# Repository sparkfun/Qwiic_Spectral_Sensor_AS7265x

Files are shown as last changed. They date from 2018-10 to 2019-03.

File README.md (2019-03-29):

SparkFun Triad Spectroscopy Sensor - AS7265x (Qwiic)
===========================================================

SparkFun Triad Spectroscopy Sensor (https://www.sparkfun.com/products/15050)

[*SparkFun Triad Spectroscopy Sensor (SEN-15050)*](https://www.sparkfun.com/products/15050)

The SparkFun Triad Spectroscopy Sensor is a powerful optical inspection sensor. Three AS7265x sensors are combined alongside a visible, UV, and IR LEDs to illuminate and test various surfaces for light spectroscopy. The Triad detects 18 discrete channels of light from 372nm (UV) to 966nm (IR) enabling desktop spectroscopy.

What can you do with light spectroscopy? It’s an amazing field of study, and the SparkFun Triad brings what used to be prohibitively expensive equipment to the desktop. The AS7265x should not be confused with highly complex mass spectrometers, but the sensor array does give the user the ability to measure and characterize how different materials absorb and reflect 18 different frequencies of light.

Want to use this board using python? Checkout hwreverse [pySectralTriad](https://github.com/hwreverse/pySpectralTriad)!

**Thanks to:**

* **pySpectralTriad** for the python application

Repository Contents
-------------------

* **/Documents** - Sensor and LED datasheets
* **/Hardware** - Eagle files

Documentation
--------------

* **[Installing an Arduino Library Guide](https://learn.sparkfun.com/tutorials/installing-an-arduino-library)** - Basic information on how to install an Arduino library.
* **[Arduino Library](https://github.com/sparkfun/SparkFun_AS7265x_Arduino_Library)** - Arduino Library for the SparkFun Triad Spectroscopy Sensor.
* **[Hookup Guide](https://learn.sparkfun.com/tutorials/spectral-triad-as7265x-hookup-guide)** - Basic hookup guide for the SparkFun Triad Spectroscopy Sensor.

License Information
-------------------

This product is _**open source**_! 

Various bits of the code have different licenses applied. Anything SparkFun wrote is beerware; if you see me (or any other SparkFun employee) at the local, and you've found our code helpful, please buy us a round!

Please use, reuse, and modify these files as you see fit. Please maintain attribution to SparkFun Electronics and release anything derivative under the same license.

Distributed as-is; no warranty is given.

- Your friends at SparkFun.

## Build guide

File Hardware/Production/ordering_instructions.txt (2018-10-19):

panel size, 86x96mm
PCB thickness, 1.6mm
number of layers, 2
soldermask color, Red
silkscreen color, White
oz copper, 1oz
finish, HASL lead free
stencils, top+bottom
pcs per panel, 4

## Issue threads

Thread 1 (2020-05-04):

### ISSUE TITLE
Schematic wrong pinout

### ISSUE THREAD

**Issue by uavmax** [sparkfun/Qwiic_Spectral_Sensor_AS7265x#1]
[https://cdn.sparkfun.com/assets/3/b/0/3/e/Qwiic_Spectral_Sensor-AS7265x.pdf](url)
SCL_M and SDA_M are not 1,20(SLV1_RESN, SLV2_RESN) pins but 9,10.
no ADDR, CS_SD pins just CSN(CD_EE). INT pin 13 not 9

**Comment by nseidle** [comment]
There has been a lot of confusion created by AMS because they released early datasheets that showed incorrect pinouts. I believe those are the datasheets you are looking at. Please see the notes on the documents tab of our [product page](https://www.sparkfun.com/products/15050). Namely:

Datasheets:

* [AS7265x](https://cdn.sparkfun.com/assets/c/2/9/0/a/AS7265x_Datasheet.pdf) (Pin assignments are misleading; use Design Considerations below.)
* [Design Considerations](https://cdn.sparkfun.com/assets/8/5/f/0/3/AS7265x_Design_Considerations.pdf)

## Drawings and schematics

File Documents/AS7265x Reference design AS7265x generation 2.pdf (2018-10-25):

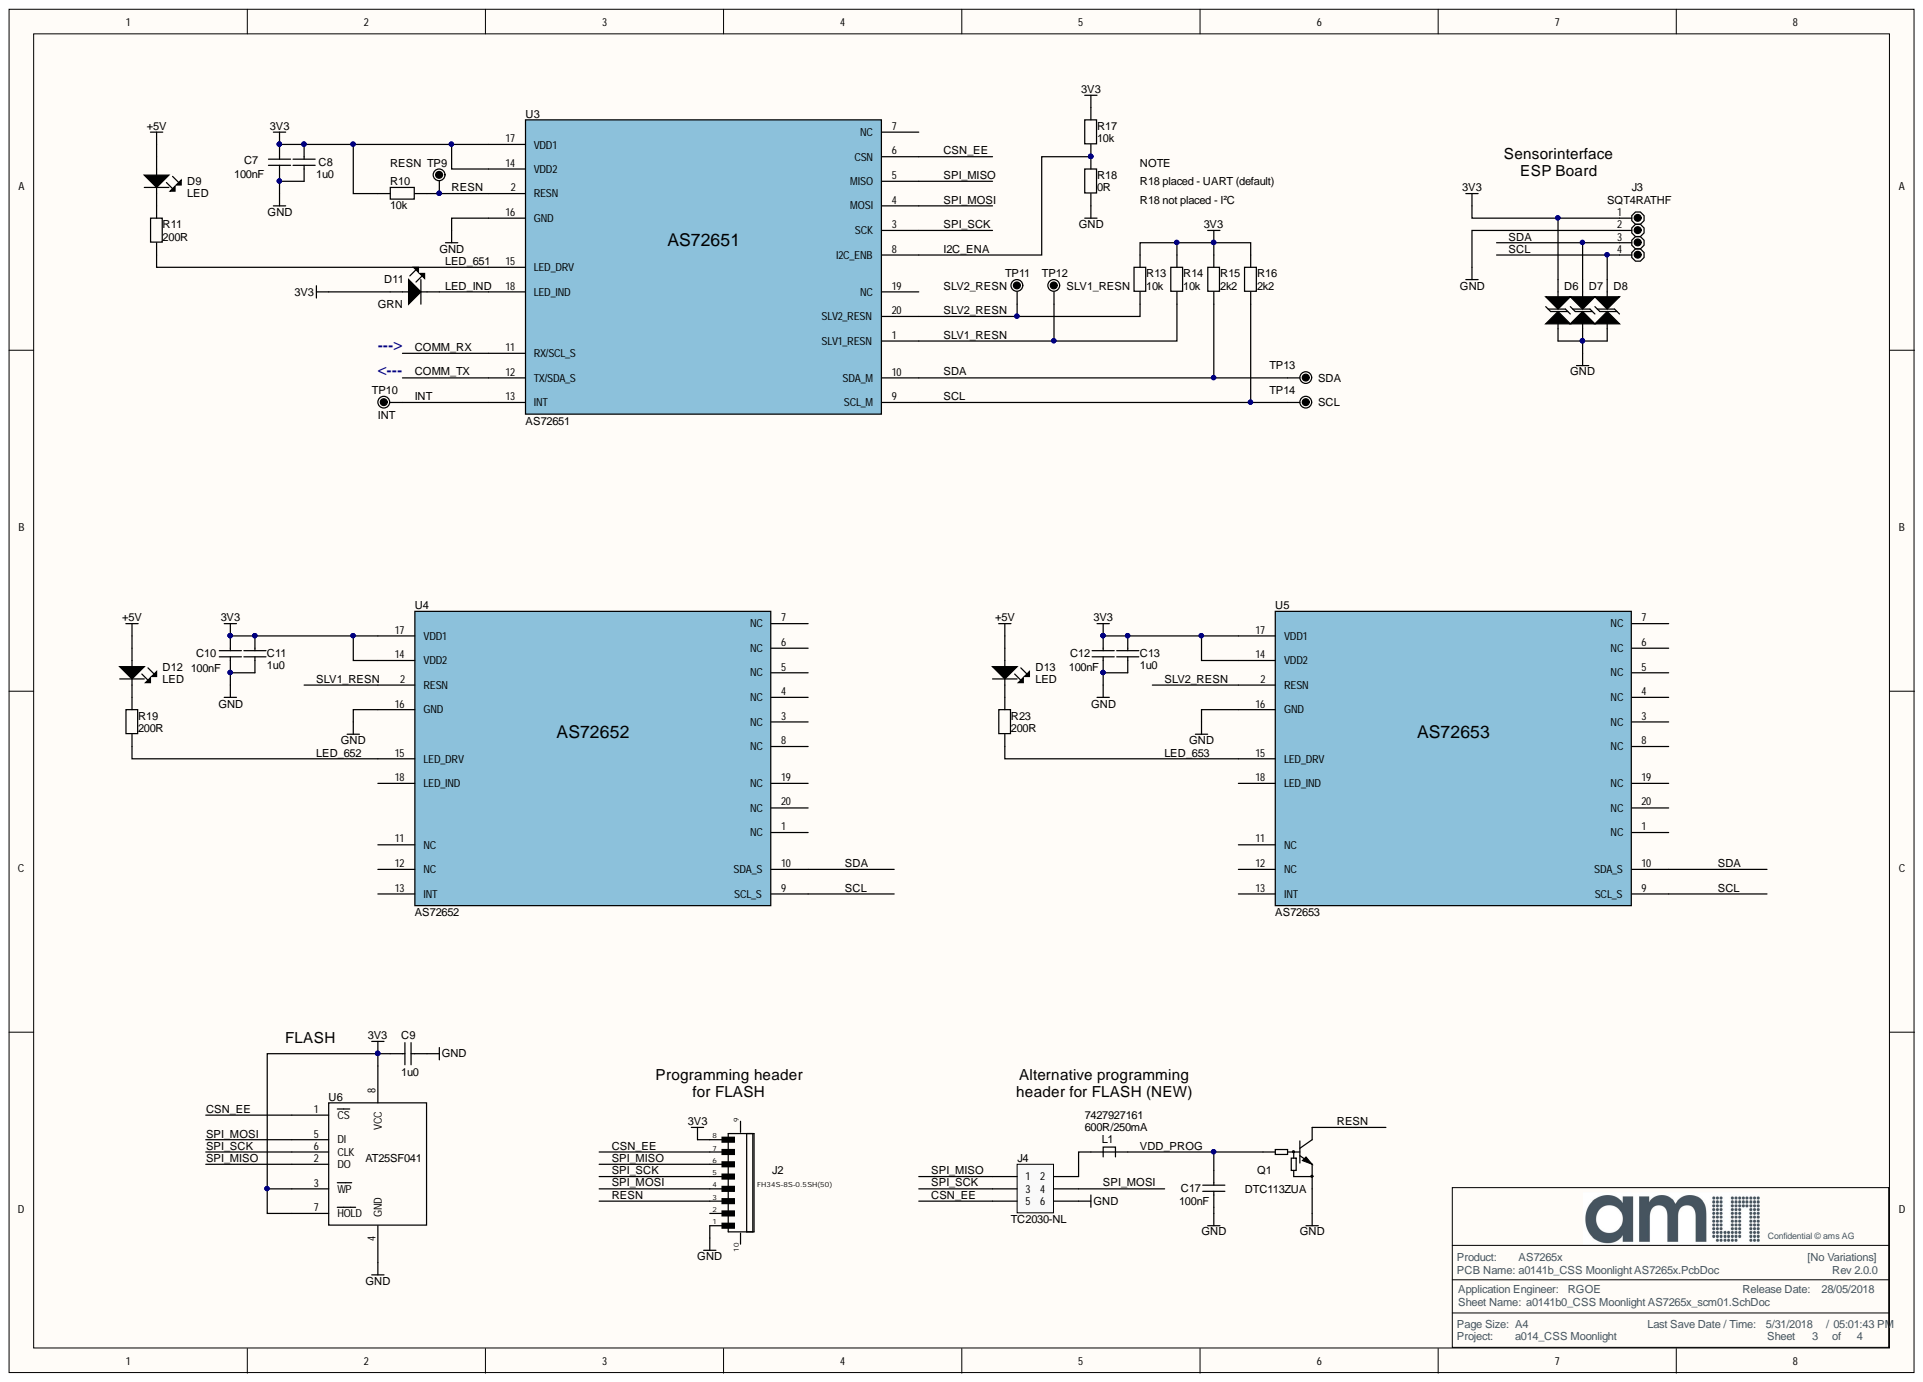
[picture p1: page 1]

VDD2 14

GND 16

Alternative programming
header for FLASH (NEW)

PCB Name:
Application Engineer: RGOE
Sheet Name: a0141b0_CSS Moonlight AS7265x_scm01.SchDoc

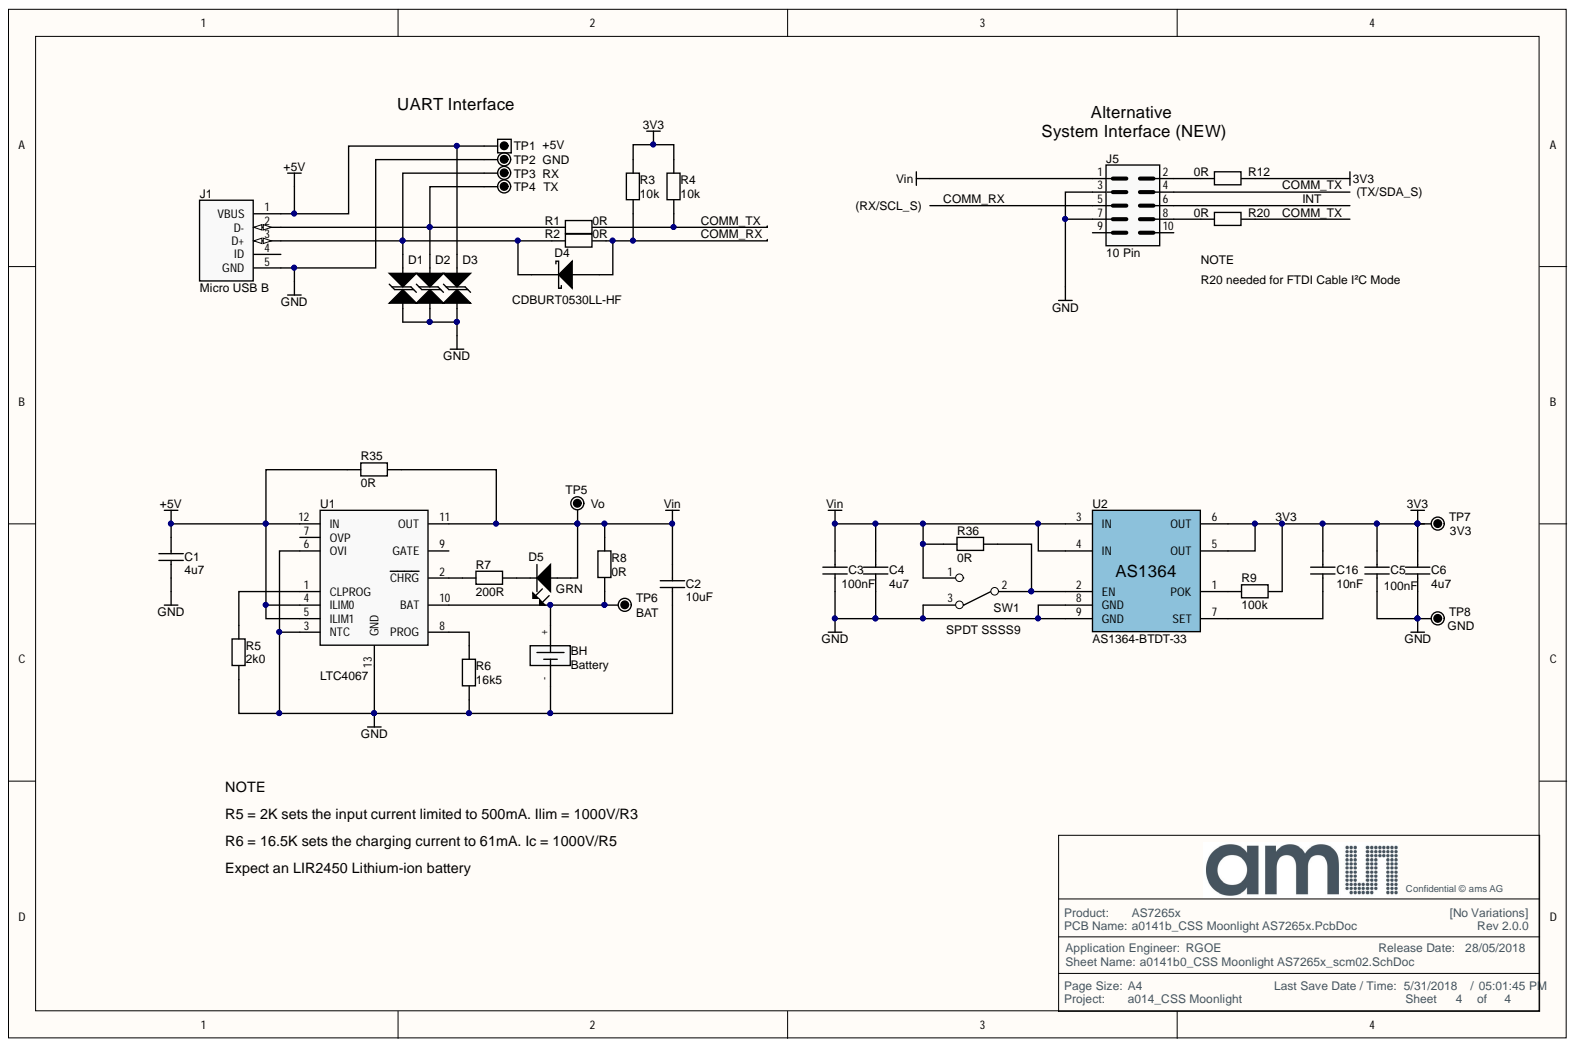
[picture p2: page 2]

NOTE
R20 needed for FTDI Cable I²C Mode

OVI 6

ILIM0 4

R5 = 2K sets the input current limited to 500mA. Ilim = 1000V/R3

R6 = 16.5K sets the charging current to 61mA. Ic = 1000V/R5

Expect an LIR2450 Lithium-ion battery

Application Engineer: RGOE
Sheet Name: a0141b0_CSS Moonlight AS7265x_scm02.SchDoc

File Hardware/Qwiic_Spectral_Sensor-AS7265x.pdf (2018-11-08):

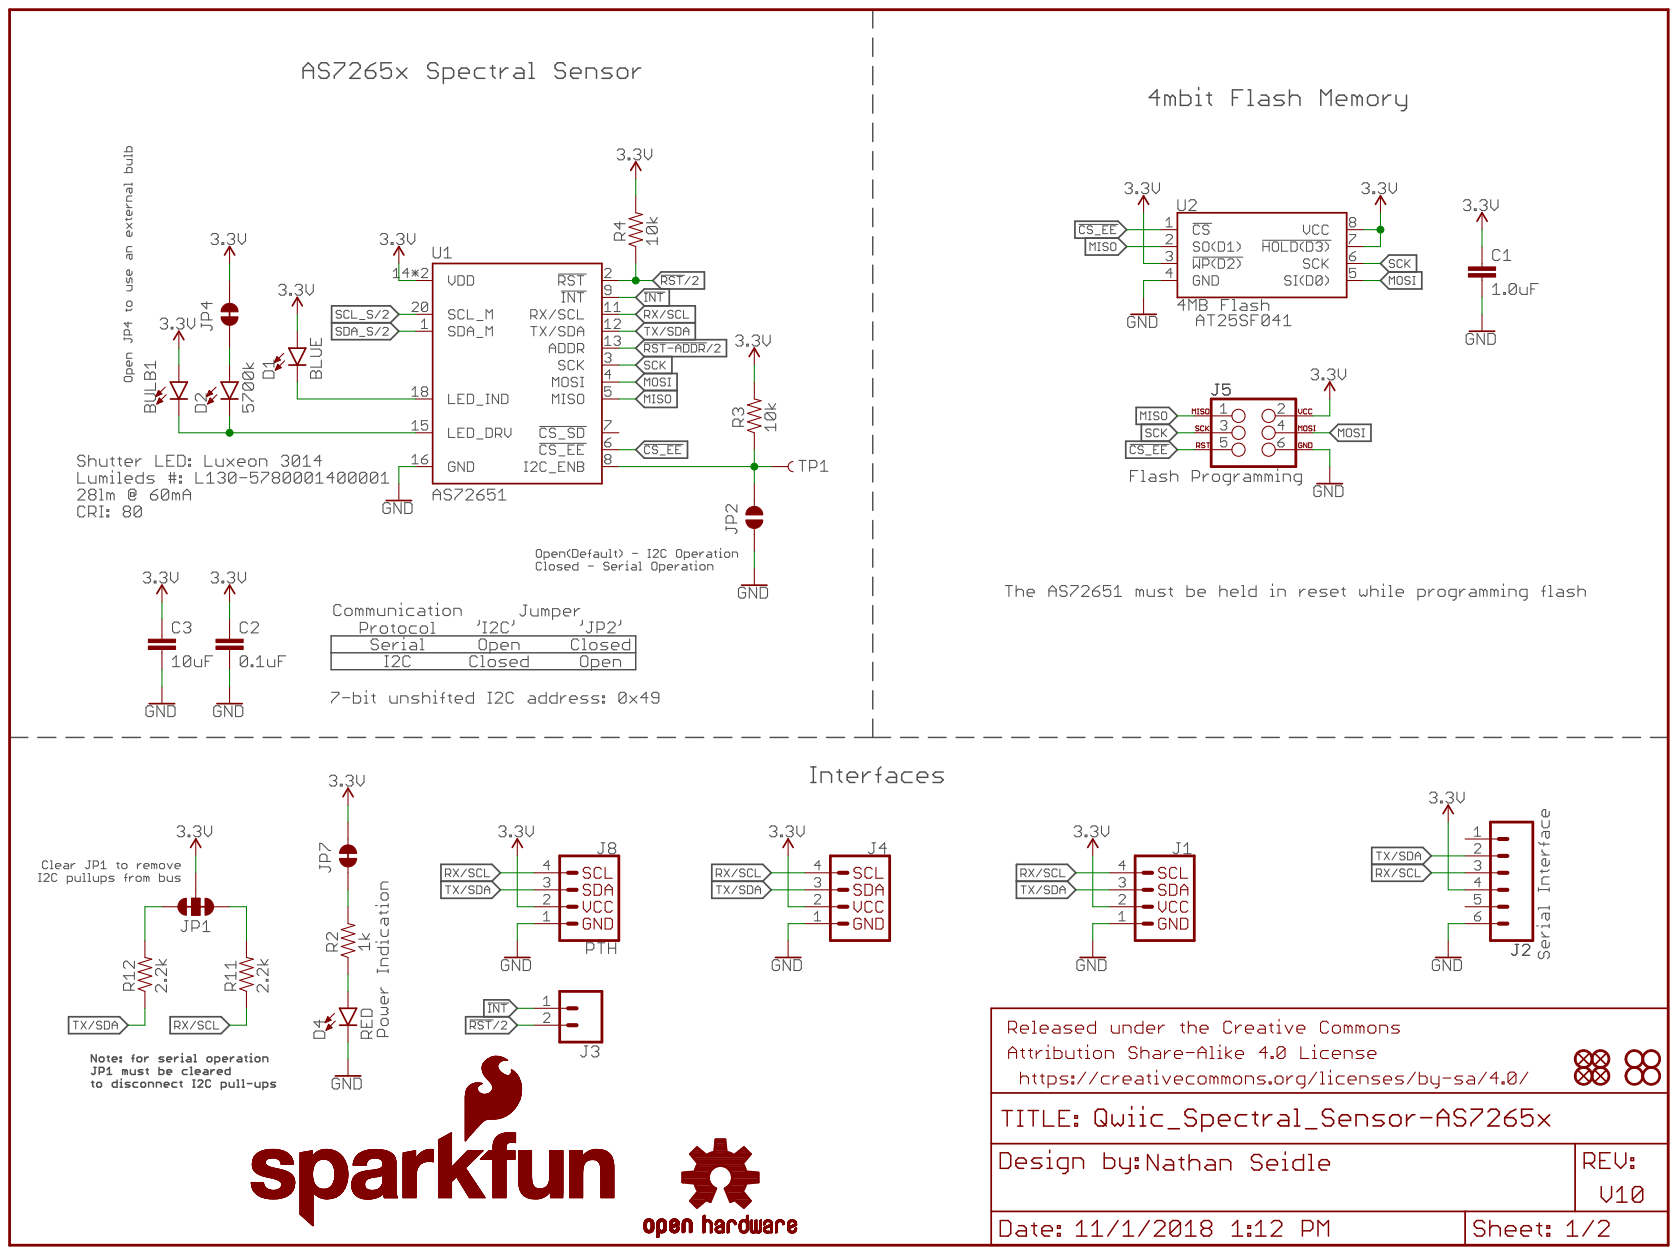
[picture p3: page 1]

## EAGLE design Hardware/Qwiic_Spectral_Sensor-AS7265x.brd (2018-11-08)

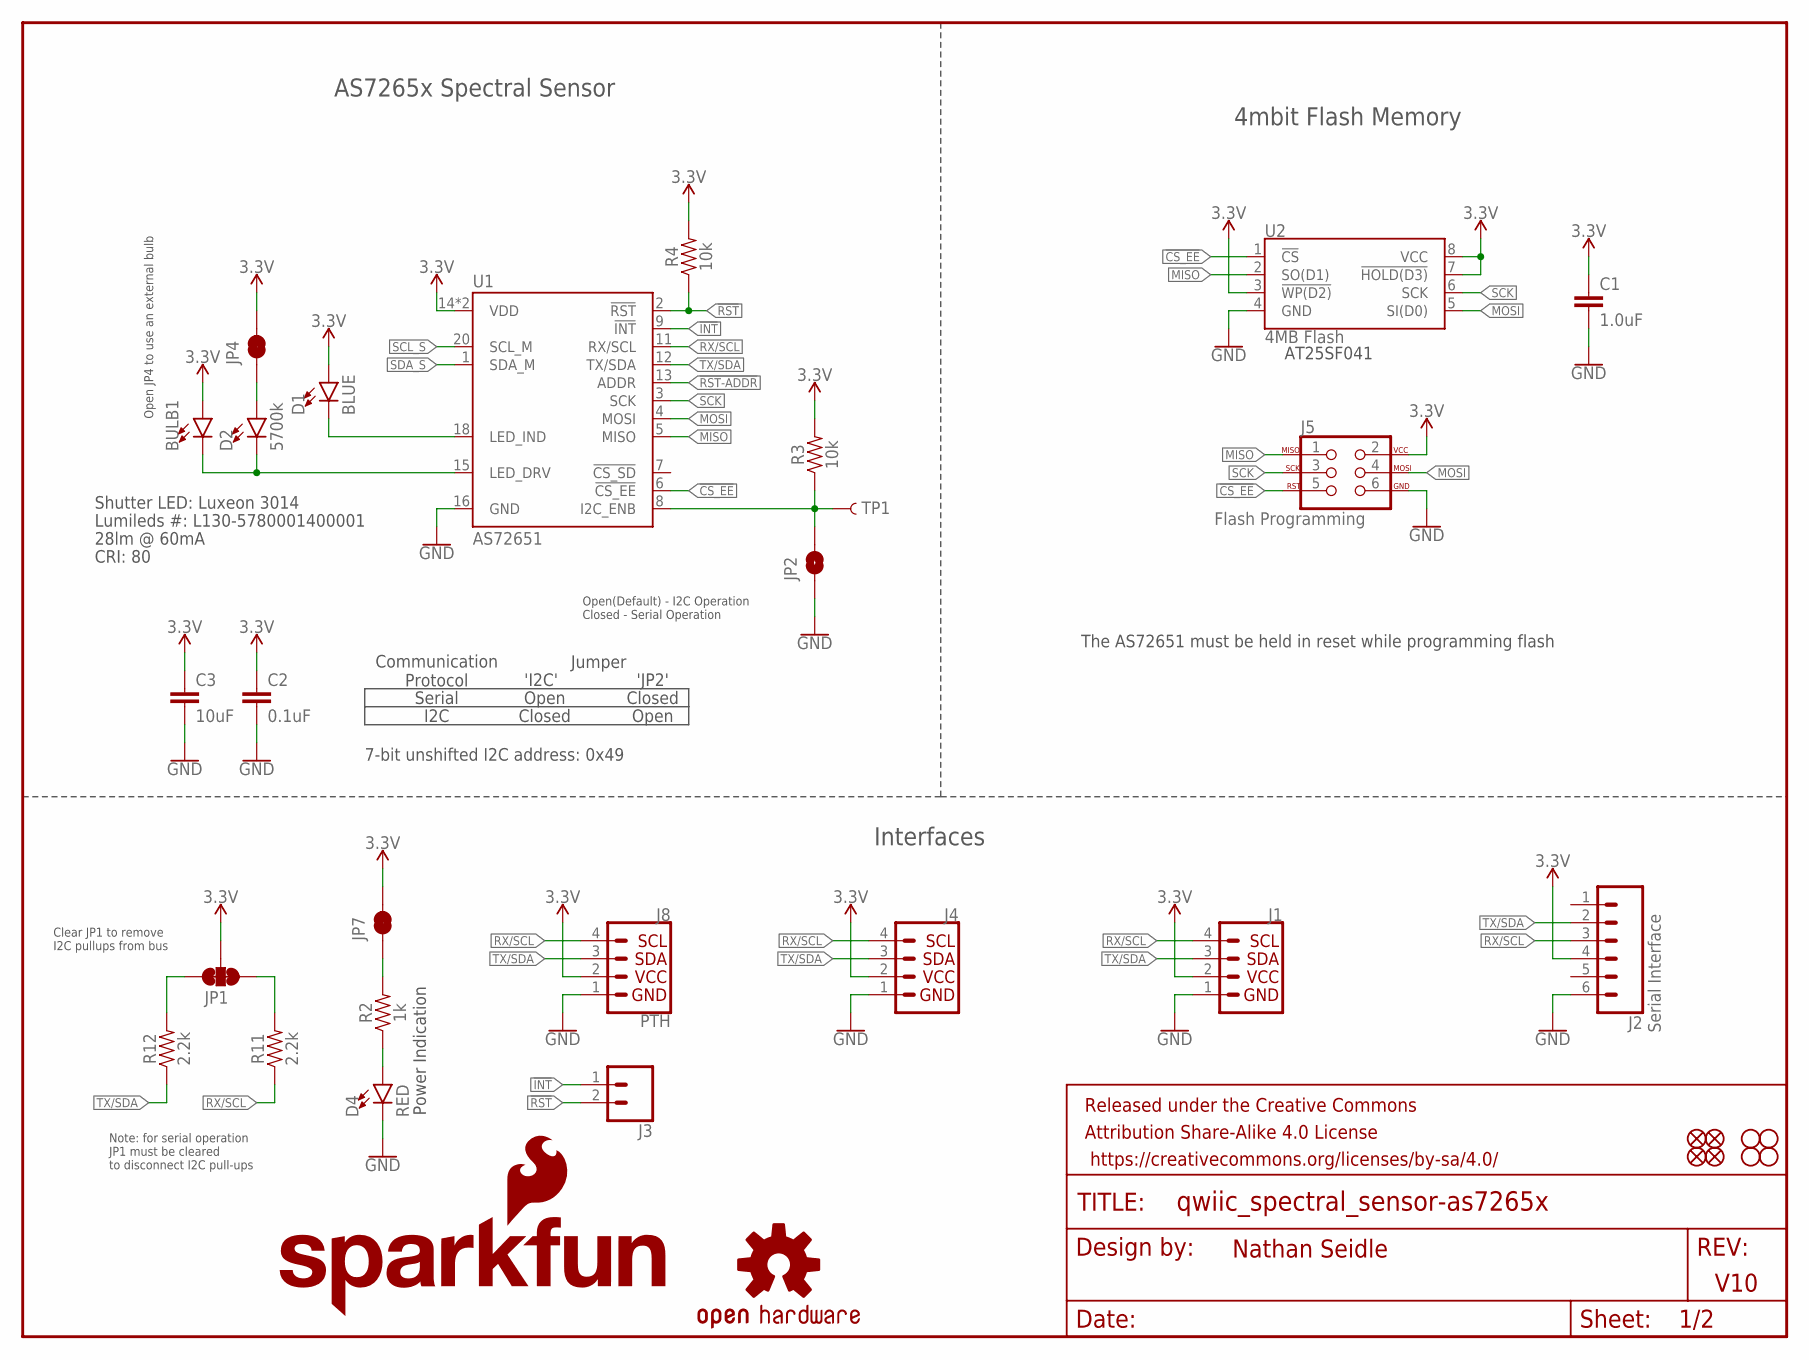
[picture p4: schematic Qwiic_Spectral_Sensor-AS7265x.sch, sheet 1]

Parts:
BULB1: LEDNS; LED_5MM_NOSILK
C1: 1.0uF; 0603
C2: 0.1uF; 0603
C3: 10uF; 0603
D1: BLUE; LED-0603
D2: 5700k; SUPER_BRIGHT_SMD_LED_3014
D4: RED; LED-0603
FD1, FD2, FD3, FD4: FIDUCIAL1X2; FIDUCIAL-1X2
FRAME1: FRAME-LETTER; CREATIVE_COMMONS
H1, H2, H3, H4: STAND-OFF
J1, J4: QWIIC_CONNECTORJS-1MM; 1X04_1MM_RA
J2: Serial Interface; 1X06_NO_SILK
J3: CONN_021X02_NO_SILK; 1X02_NO_SILK
J5: Flash Programming; 2X3_TEST_POINTS
J8: PTH; 1X04_NO_SILK
JP1: JUMPER-SMT_3_2-NC_TRACE_SILK; SMT-JUMPER_3_2-NC_TRACE_SILK
JP2: JUMPER-SMT_2_NO_SILK; SMT-JUMPER_2_NO_SILK
JP4, JP7: JUMPER-SMT_2_NC_TRACE_NO-SILK; SMT-JUMPER_2_NC_TRACE_NO-SILK
LOGO1: SFE_LOGO_NAME_FLAME.1_INCH; SFE_LOGO_NAME_FLAME_.1
LOGO4: OSHW-LOGOS; OSHW-LOGO-S
R2: 1k; 0603
R3, R4: 10k; 0603
R11, R12: 2.2k; 0603
TP1: TEST-POINT3; PAD.03X.03
U1: AS72651; LGA20
U2: 4MB Flash; SO08

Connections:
3.3V: BULB1.A, C1.1, C2.1, C3.1, D1.A, J1.2, J2.4, J4.2, J5.2, J8.2, JP1.2, JP4.2, JP7.2, R3.2, R4.2, U1.14 (VDD), U1.17 (VDD), U2.3 (!WP(D2)), U2.7 (!HOLD(D3)), U2.8 (VCC); also elsewhere on the board
!CS_EE: J5.5, U1.6 (!CS_EE), U2.1 (!CS)
!INT: J3.1, U1.9 (!INT)
!RST: J3.2, R4.1, U1.2 (!RST); also elsewhere on the board
!RST-ADDR: U1.13 (ADDR); also elsewhere on the board
GND: C1.2, C2.2, C3.2, D4.C, J1.1, J2.6, J4.1, J5.6, J8.1, JP2.1, U1.16 (GND), U2.4 (GND); also elsewhere on the board
I2C_ENB: JP2.2, R3.1, TP1.P$1, U1.8 (I2C_ENB)
LED_DRV: BULB1.K (C), D2.C, U1.15 (LED_DRV)
MISO: J5.1, U1.5 (MISO), U2.2 (SO(D1))
MOSI: J5.4, U1.4 (MOSI), U2.5 (SI(D0))
unnamed: JP7.1, R2.2
unnamed: D1.C, U1.18 (LED_IND)
unnamed: JP1.3, R12.2
unnamed: JP1.1, R11.2
unnamed: D2.A, JP4.1
unnamed: D4.A, R2.1
RX/SCL: J1.4, J2.3, J4.4, J8.4, R11.1, U1.11 (RX/SCL)
SCK: J5.3, U1.3 (SCK), U2.6 (SCK)
SCL_S: U1.20 (SCL_M); also elsewhere on the board
SDA_S: U1.1 (SDA_M); also elsewhere on the board
TX/SDA: J1.3, J2.2, J4.3, J8.3, R12.1, U1.12 (TX/SDA)

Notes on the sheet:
AS7265x Spectral Sensor
Open(Default) - I2C Operation Closed - Serial Operation
Clear JP1 to remove I2C pullups from bus
V10
Nathan Seidle
4mbit Flash Memory
Interfaces
Note: for serial operation JP1 must be cleared to disconnect I2C pull-ups
The AS72651 must be held in reset while programming flash
Open JP4 to use an external bulb
Serial
'I2C'
'JP2'
Open
Closed
Communication Protocol
I2C
Lumileds #: L130-5780001400001
Shutter LED: Luxeon 3014
28lm @ 60mA
CRI: 80
7-bit unshifted I2C address: 0x49
Power Indication
AT25SF041
Jumper

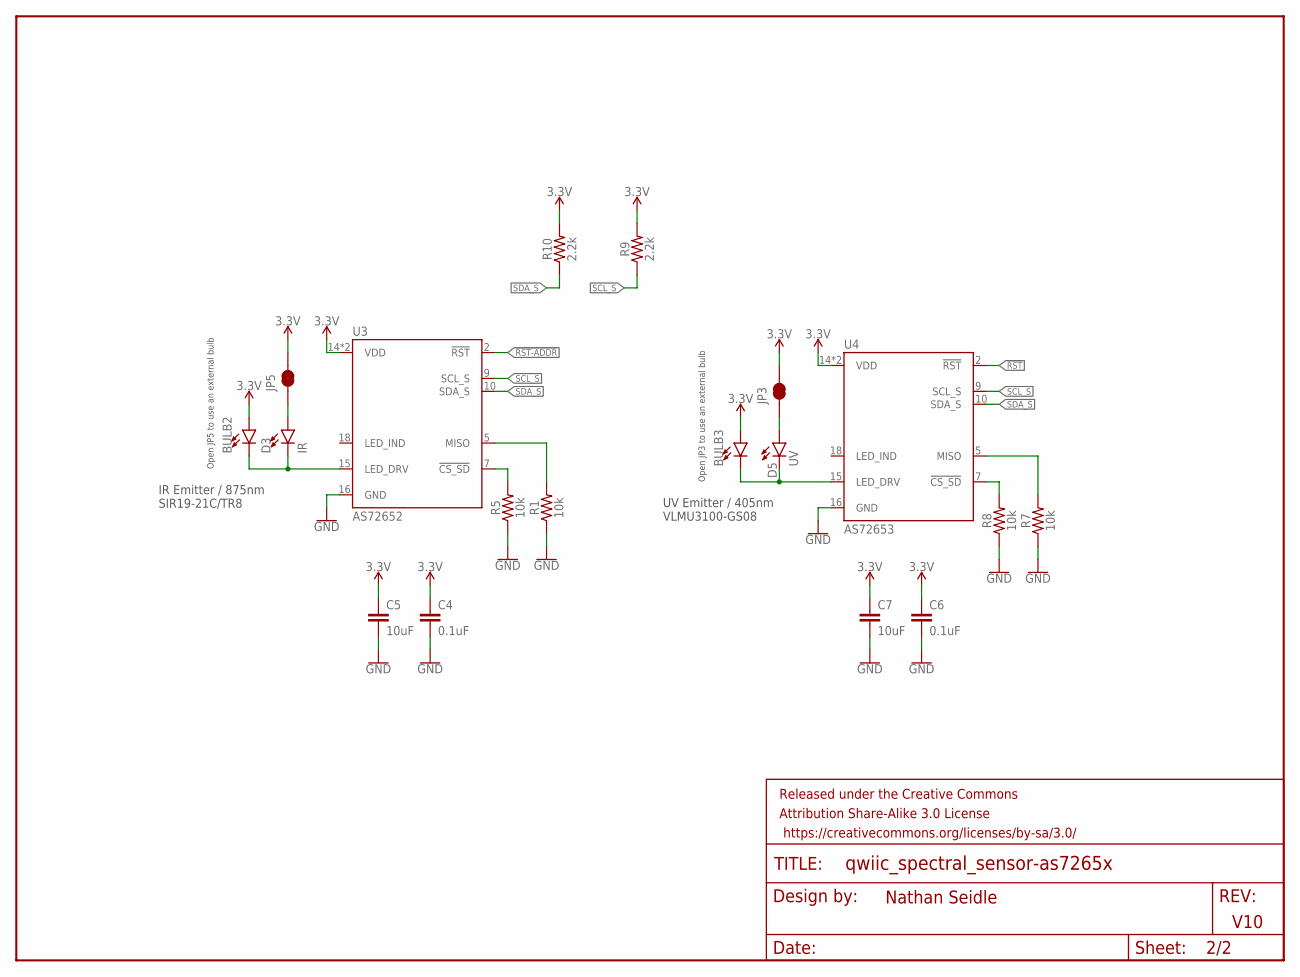
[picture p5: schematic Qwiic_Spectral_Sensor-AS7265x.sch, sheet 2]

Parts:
BULB2, BULB3: LEDNS; LED_5MM_NOSILK
C4, C6: 0.1uF; 0603
C5, C7: 10uF; 0603
D3: IR; LED-0603
D5: UV; PLCC-2
FRAME3: FRAME-LETTER; CREATIVE_COMMONS
JP3, JP5: JUMPER-SMT_2_NC_TRACE_NO-SILK; SMT-JUMPER_2_NC_TRACE_NO-SILK
R1, R5, R7, R8: 10k; 0603
R9, R10: 2.2k; 0603
U3: AS72652; LGA20
U4: AS72653; LGA20

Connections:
3.3V: BULB2.A, BULB3.A, C4.1, C5.1, C6.1, C7.1, JP3.2, JP5.2, R9.2, R10.2, U3.14 (VDD), U3.17 (VDD), U4.14 (VDD), U4.17 (VDD); also elsewhere on the board
!RST: U4.2 (!RST); also elsewhere on the board
!RST-ADDR: U3.2 (!RST); also elsewhere on the board
GND: C4.2, C5.2, C6.2, C7.2, R1.1, R5.1, R7.1, R8.1, U3.16 (GND), U4.16 (GND); also elsewhere on the board
LED_DRV1: BULB2.K (C), D3.C, U3.15 (LED_DRV)
LED_DRV2: BULB3.K (C), D5.C, U4.15 (LED_DRV)
unnamed: R5.2, U3.7 (!CS_SD)
unnamed: D3.A, JP5.1
unnamed: R1.2, U3.5 (MISO)
unnamed: D5.A, JP3.1
unnamed: R8.2, U4.7 (!CS_SD)
unnamed: R7.2, U4.5 (MISO)
SCL_S: R9.1, U3.9 (SCL_S), U4.9 (SCL_S); also elsewhere on the board
SDA_S: R10.1, U3.10 (SDA_S), U4.10 (SDA_S); also elsewhere on the board

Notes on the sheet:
Open JP5 to use an external bulb
Open JP3 to use an external bulb
IR Emitter / 875nm SIR19-21C/TR8
UV Emitter / 405nm VLMU3100-GS08
V10
Nathan Seidle

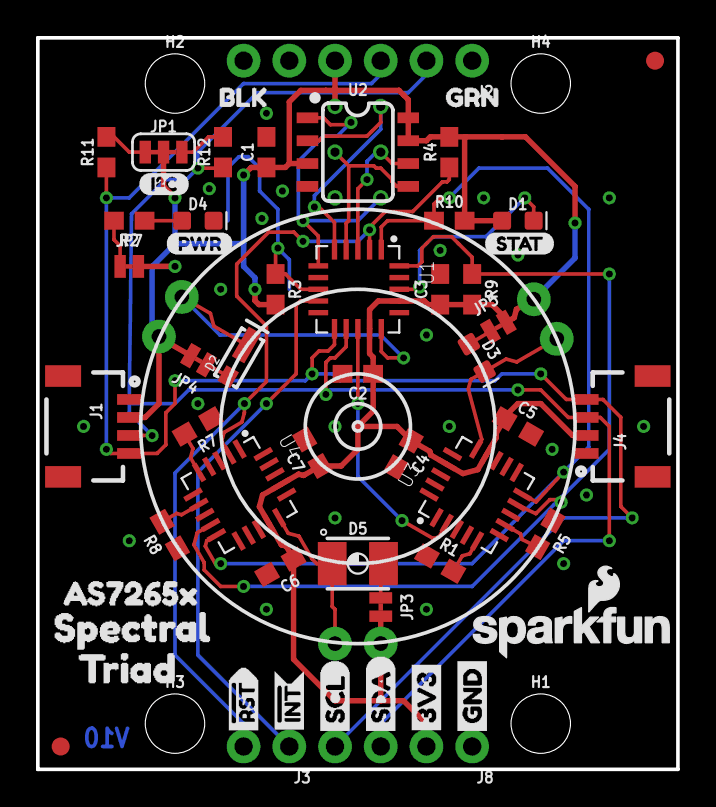
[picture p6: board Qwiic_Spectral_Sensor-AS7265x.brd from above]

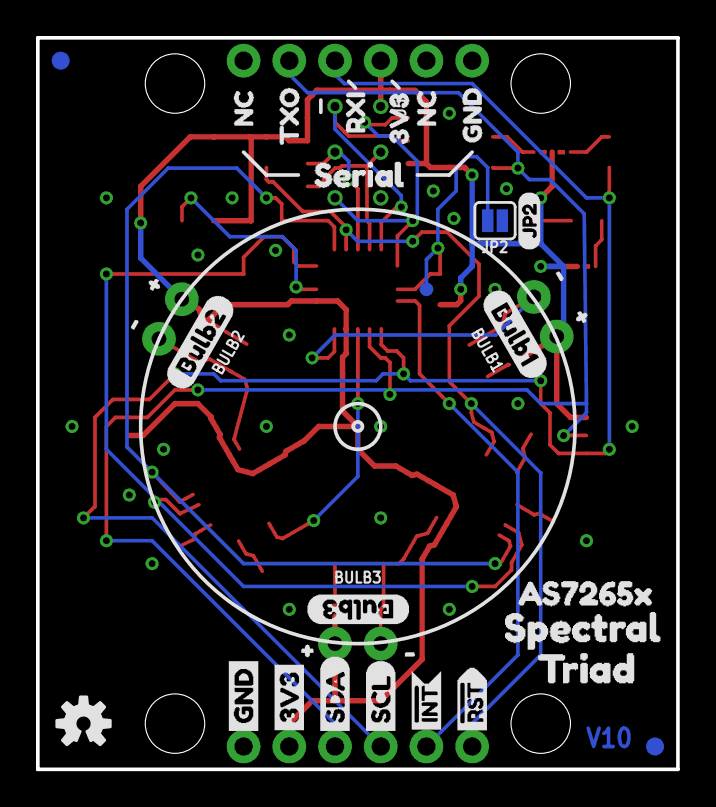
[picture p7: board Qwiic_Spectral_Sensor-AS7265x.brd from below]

Board: 2 copper layers, 35.6 x 40.6 mm, 95 parts (35 on the bottom side), 29 nets.

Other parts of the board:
U$1, U$36, U$37: #0
U$2: I_SUPER2_C-()-03
U$3: PWR-()-03
U$4, U$14: AS7265X0
U$5: BULB15
U$6: BULB26
U$7: BULB37
U$8: JP20
U$9, U$13: SPECTRAL1
U$10: STAT4
U$11, U$12: TRIAD2
U$15: 3V33
U$16: BLK7
U$17: GND5
U$18: GRN6
U$19, U$20: NC4
U$21: RXI2
U$22: SERIAL0
U$23: TXO1
U$24, U$31: 3V3-04
U$25, U$30: GND-04
U$26, U$32: SDA-[)
U$27, U$33: SCL-[)
U$28, U$34: INT#-[<-04
U$29, U$35: RST#-[>-04
U$38, U$39, U$40: #1

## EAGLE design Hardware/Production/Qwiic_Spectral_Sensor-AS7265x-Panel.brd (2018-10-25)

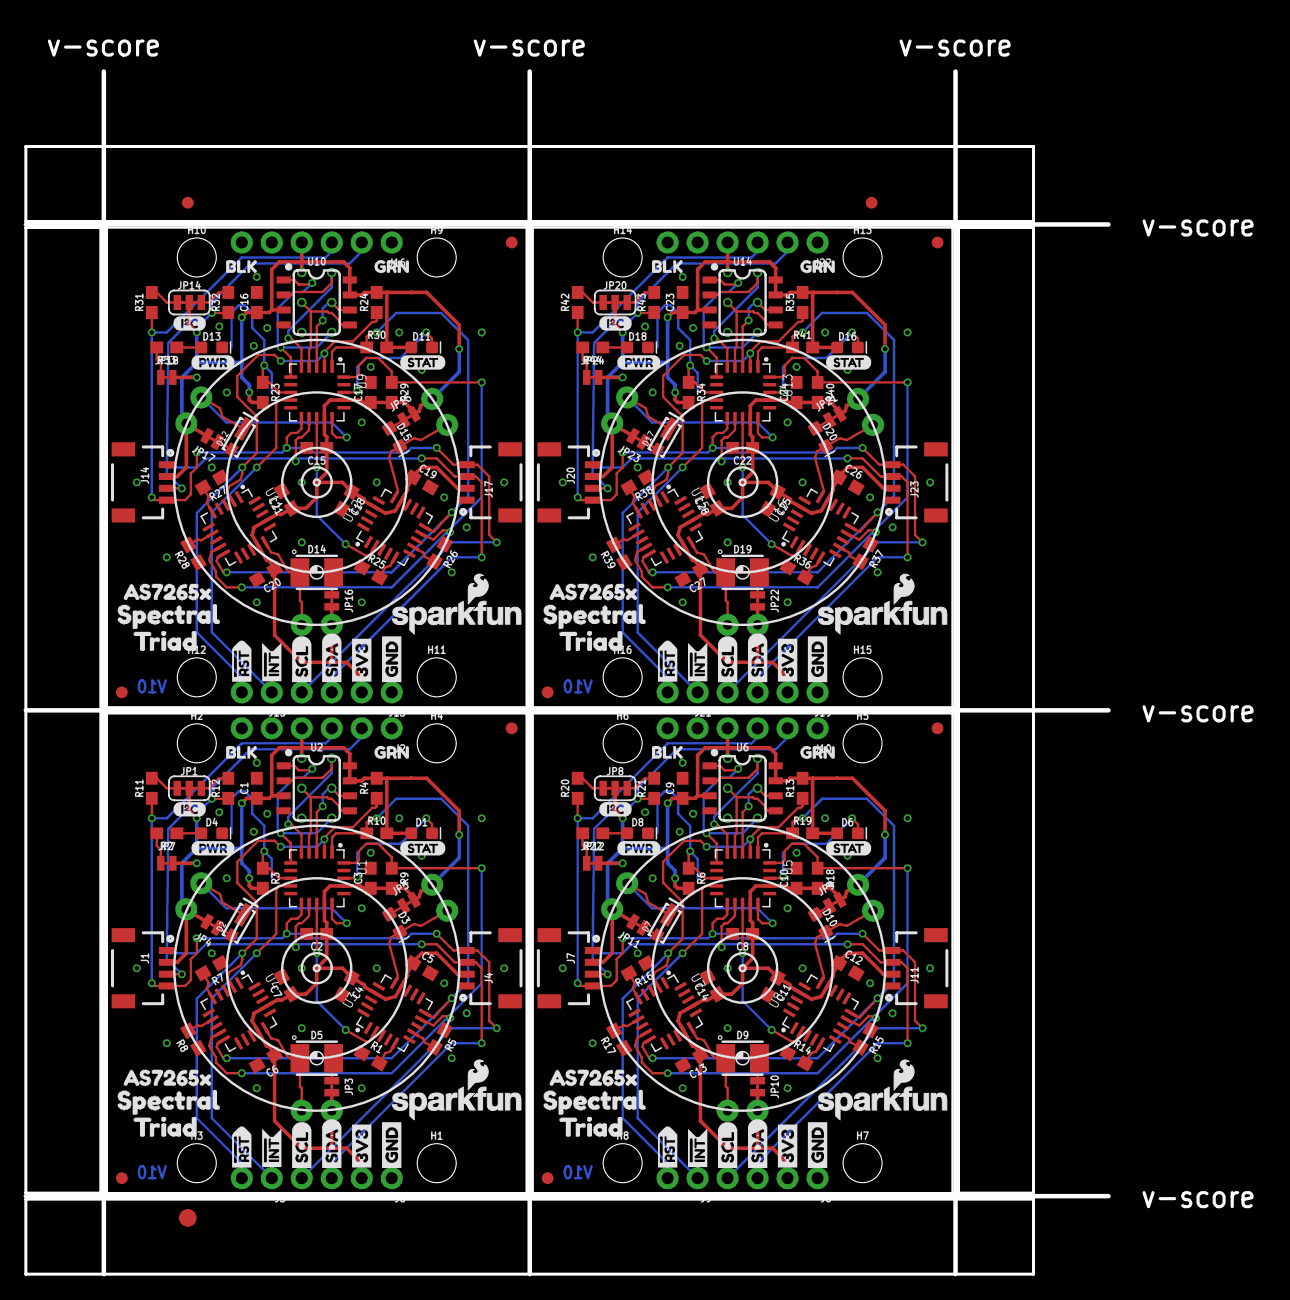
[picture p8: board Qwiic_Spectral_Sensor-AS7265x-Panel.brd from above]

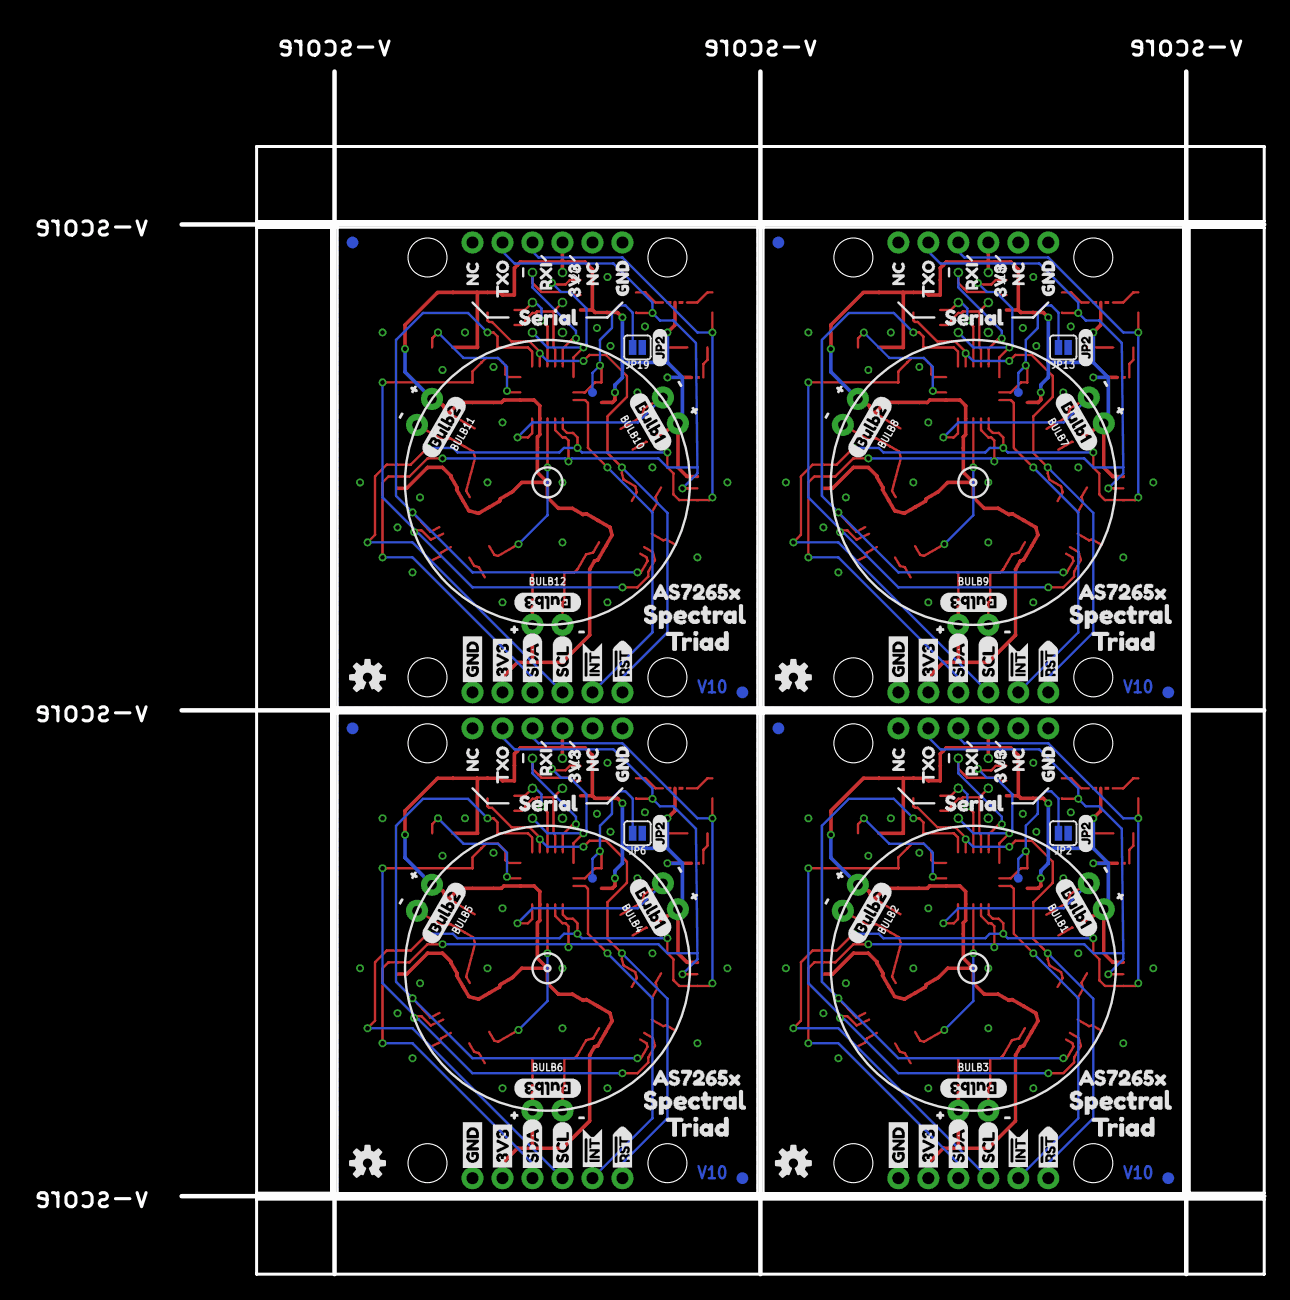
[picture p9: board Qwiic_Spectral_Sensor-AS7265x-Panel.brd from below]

Board: 2 copper layers, 91.7 x 101.9 mm, 375 parts (140 on the bottom side), 116 nets.

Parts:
BULB1, BULB2, BULB3, BULB4, BULB5, BULB6, BULB7, BULB8, BULB9, BULB10, BULB11, BULB12: LED_5MM_NOSILK
C1, C9, C16, C23: 1.0uF; 0603
C2, C4, C6, C8, C11, C13, C15, C18, C20, C22, C25, C27: 0.1uF; 0603
C3, C5, C7, C10, C12, C14, C17, C19, C21, C24, C26, C28: 10uF; 0603
D1, D6, D11, D16: BLUE; LED-0603
D2, D7, D12, D17: 5700k; SUPER_BRIGHT_SMD_LED_3014
D3, D10, D15, D20: IR; LED-0603
D4, D8, D13, D18: RED; LED-0603
D5, D9, D14, D19: UV; PLCC-2
E$1, E$2: FIDUCIAL-1X2
E$3: FIDUCIAL-1.5X3
FD1, FD2, FD3, FD4, FD5, FD6, FD7, FD8, FD9, FD10, FD11, FD12, FD13, FD14, FD15, FD16: FIDUCIAL1X2; FIDUCIAL-1X2
H1, H2, H3, H4, H5, H6, H7, H8, H9, H10, H11, H12, H13, H14, H15, H16: STAND-OFF
J1, J4, J7, J11, J14, J17, J20, J23: 1X04_1MM_RA
J2, J10, J16, J22: Serial Interface; 1X06_NO_SILK
J3, J9, J15, J21: 1X02_NO_SILK
J5, J12, J18, J24: Flash Programming; 2X3_TEST_POINTS
J6, J8, J13, J19: PTH; 1X04_NO_SILK
JP1, JP8, JP14, JP20: SMT-JUMPER_3_2-NC_TRACE_SILK
JP2, JP6, JP13, JP19: SMT-JUMPER_2_NO_SILK
JP3, JP4, JP5, JP7, JP9, JP10, JP11, JP12, JP15, JP16, JP17, JP18, JP21, JP22, JP23, JP24: SMT-JUMPER_2_NC_TRACE_NO-SILK
LOGO1, LOGO3, LOGO6, LOGO8: SFE_LOGO_NAME_FLAME.1_INCH; SFE_LOGO_NAME_FLAME_.1
LOGO2, LOGO4, LOGO5, LOGO7: OSHW-LOGOS; OSHW-LOGO-S
R1, R3, R4, R5, R6, R7, R8, R13, R14, R15, R16, R17, R23, R24, R25, R26, R27, R28, R34, R35, R36, R37, R38, R39: 10k; 0603
R2, R22, R33, R44: 1k; 0603
R9, R10, R11, R12, R18, R19, R20, R21, R29, R30, R31, R32, R40, R41, R42, R43: 2.2k; 0603
TP1, TP2, TP3, TP4: PAD.03X.03
U1, U5, U9, U13: AS72651; LGA20
U2, U6, U10, U14: 4MB Flash; SO08
U3, U8, U12, U16: AS72652; LGA20
U4, U7, U11, U15: AS72653; LGA20
U$1, U$36, U$37, U$75, U$76, U$77, U$115, U$116, U$117, U$155, U$156, U$157: #0
U$2, U$41, U$81, U$121: I_SUPER2_C-()-03
U$3, U$42, U$82, U$122: PWR-()-03
U$4, U$14, U$43, U$52, U$83, U$92, U$123, U$132: AS7265X0
U$5, U$44, U$84, U$124: BULB15
U$6, U$45, U$85, U$125: BULB26
U$7, U$46, U$86, U$126: BULB37
U$8, U$62, U$102, U$142: JP20
U$9, U$13, U$47, U$51, U$87, U$91, U$127, U$131: SPECTRAL1
U$10, U$48, U$88, U$128: STAT4
U$11, U$12, U$49, U$50, U$89, U$90, U$129, U$130: TRIAD2
U$15, U$53, U$93, U$133: 3V33
U$16, U$54, U$94, U$134: BLK7
U$17, U$55, U$95, U$135: GND5
U$18, U$56, U$96, U$136: GRN6
U$19, U$20, U$57, U$58, U$97, U$98, U$137, U$138: NC4
U$21, U$59, U$99, U$139: RXI2
U$22, U$60, U$100, U$140: SERIAL0
U$23, U$61, U$101, U$141: TXO1
U$24, U$31, U$63, U$70, U$103, U$110, U$143, U$150: 3V3-04
U$25, U$30, U$64, U$69, U$104, U$109, U$144, U$149: GND-04
U$26, U$32, U$65, U$71, U$105, U$111, U$145, U$151: SDA-[)
U$27, U$33, U$66, U$72, U$106, U$112, U$146, U$152: SCL-[)
U$28, U$34, U$67, U$73, U$107, U$113, U$147, U$153: INT#-[<-04
U$29, U$35, U$68, U$74, U$108, U$114, U$148, U$154: RST#-[>-04
U$38, U$39, U$40, U$78, U$79, U$80, U$118, U$119, U$120, U$158, U$159, U$160: #1

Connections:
3.3V: BULB1.A, BULB2.A, BULB3.A, C1.1, C2.1, C3.1, C4.1, C5.1, C6.1, C7.1, D1.A, J1.2, J2.4, J4.2, J5.2, J8.2, JP1.2, JP3.2, JP4.2, JP5.2, JP7.2, R3.2, R4.2, R9.2, R10.2, U1.14, U1.17, U2.3, U2.7, U2.8, U3.14, U3.17, U4.14, U4.17
3.3V1: BULB4.A, BULB5.A, BULB6.A, C8.1, C9.1, C10.1, C11.1, C12.1, C13.1, C14.1, D6.A, J6.2, J7.2, J10.4, J11.2, J12.2, JP8.2, JP9.2, JP10.2, JP11.2, JP12.2, R6.2, R13.2, R18.2, R19.2, U5.14, U5.17, U6.3, U6.7, U6.8, U7.14, U7.17, U8.14, U8.17
3.3V2: BULB7.A, BULB8.A, BULB9.A, C15.1, C16.1, C17.1, C18.1, C19.1, C20.1, C21.1, D11.A, J13.2, J14.2, J16.4, J17.2, J18.2, JP14.2, JP15.2, JP16.2, JP17.2, JP18.2, R23.2, R24.2, R29.2, R30.2, U9.14, U9.17, U10.3, U10.7, U10.8, U11.14, U11.17, U12.14, U12.17
3.3V3: BULB10.A, BULB11.A, BULB12.A, C22.1, C23.1, C24.1, C25.1, C26.1, C27.1, C28.1, D16.A, J19.2, J20.2, J22.4, J23.2, J24.2, JP20.2, JP21.2, JP22.2, JP23.2, JP24.2, R34.2, R35.2, R40.2, R41.2, U13.14, U13.17, U14.3, U14.7, U14.8, U15.14, U15.17, U16.14, U16.17
!CS_EE: J5.5, U1.6, U2.1
!CS_EE1: J12.5, U5.6, U6.1
!CS_EE2: J18.5, U9.6, U10.1
!CS_EE3: J24.5, U13.6, U14.1
!INT: J3.1, U1.9
!INT1: J9.1, U5.9
!INT2: J15.1, U9.9
!INT3: J21.1, U13.9
!RST: J3.2, R4.1, U1.2, U4.2
!RST1: J9.2, R13.1, U5.2, U7.2
!RST2: J15.2, R24.1, U9.2, U11.2
!RST3: J21.2, R35.1, U13.2, U15.2
!RST-ADDR: U1.13, U3.2
!RST-ADDR1: U5.13, U8.2
!RST-ADDR2: U9.13, U12.2
!RST-ADDR3: U13.13, U16.2
GND: C1.2, C2.2, C3.2, C4.2, C5.2, C6.2, C7.2, D4.C, J1.1, J2.6, J4.1, J5.6, J8.1, JP2.1, R1.1, R5.1, R7.1, R8.1, U1.16, U2.4, U3.16, U4.16
GND1: C8.2, C9.2, C10.2, C11.2, C12.2, C13.2, C14.2, D8.C, J6.1, J7.1, J10.6, J11.1, J12.6, JP6.1, R14.1, R15.1, R16.1, R17.1, U5.16, U6.4, U7.16, U8.16
GND2: C15.2, C16.2, C17.2, C18.2, C19.2, C20.2, C21.2, D13.C, J13.1, J14.1, J16.6, J17.1, J18.6, JP13.1, R25.1, R26.1, R27.1, R28.1, U9.16, U10.4, U11.16, U12.16
GND3: C22.2, C23.2, C24.2, C25.2, C26.2, C27.2, C28.2, D18.C, J19.1, J20.1, J22.6, J23.1, J24.6, JP19.1, R36.1, R37.1, R38.1, R39.1, U13.16, U14.4, U15.16, U16.16
I2C_ENB: JP2.2, R3.1, TP1.P$1, U1.8
I2C_ENB1: JP6.2, R6.1, TP2.P$1, U5.8
I2C_ENB2: JP13.2, R23.1, TP3.P$1, U9.8
I2C_ENB3: JP19.2, R34.1, TP4.P$1, U13.8
LED_DRV: BULB1.K, D2.C, U1.15
LED_DRV1: BULB2.K, D3.C, U3.15
LED_DRV2: BULB3.K, D5.C, U4.15
LED_DRV3: BULB4.K, D7.C, U5.15
LED_DRV4: BULB5.K, D10.C, U8.15
LED_DRV5: BULB6.K, D9.C, U7.15
LED_DRV6: BULB7.K, D12.C, U9.15
LED_DRV7: BULB8.K, D15.C, U12.15
LED_DRV8: BULB9.K, D14.C, U11.15
LED_DRV9: BULB10.K, D17.C, U13.15
LED_DRV10: BULB11.K, D20.C, U16.15
LED_DRV11: BULB12.K, D19.C, U15.15
MISO: J5.1, U1.5, U2.2
MISO1: J12.1, U5.5, U6.2
MISO2: J18.1, U9.5, U10.2
MISO3: J24.1, U13.5, U14.2
MOSI: J5.4, U1.4, U2.5
MOSI1: J12.4, U5.4, U6.5
MOSI2: J18.4, U9.4, U10.5
MOSI3: J24.4, U13.4, U14.5
unnamed: JP7.1, R2.2
unnamed: D1.C, U1.18
unnamed: R5.2, U3.7
unnamed: JP1.3, R12.2
unnamed: JP1.1, R11.2
unnamed: D2.A, JP4.1
unnamed: D4.A, R2.1
unnamed: D3.A, JP5.1
unnamed: R1.2, U3.5
unnamed: JP8.3, R21.2
unnamed: D5.A, JP3.1
unnamed: R8.2, U4.7
unnamed: R7.2, U4.5
unnamed: JP8.1, R20.2
unnamed: D6.C, U5.18
unnamed: D7.A, JP11.1
unnamed: D10.A, JP9.1
unnamed: R15.2, U8.7
unnamed: R14.2, U8.5
unnamed: D9.A, JP10.1
unnamed: R17.2, U7.7
unnamed: R16.2, U7.5
unnamed: JP12.1, R22.2
unnamed: D8.A, R22.1
unnamed: JP14.3, R32.2
unnamed: JP14.1, R31.2
unnamed: D11.C, U9.18
unnamed: D12.A, JP17.1
unnamed: D15.A, JP15.1
unnamed: R26.2, U12.7
unnamed: R25.2, U12.5
unnamed: D14.A, JP16.1
unnamed: R28.2, U11.7
unnamed: R27.2, U11.5
unnamed: JP18.1, R33.2
unnamed: D13.A, R33.1
unnamed: JP20.3, R43.2
unnamed: JP20.1, R42.2
unnamed: D16.C, U13.18
unnamed: D17.A, JP23.1
unnamed: D20.A, JP21.1
unnamed: R37.2, U16.7
unnamed: R36.2, U16.5
unnamed: D19.A, JP22.1
unnamed: R39.2, U15.7
unnamed: R38.2, U15.5
unnamed: JP24.1, R44.2
unnamed: D18.A, R44.1
RX/SCL: J1.4, J2.3, J4.4, J8.4, R11.1, U1.11
RX/SCL1: J6.4, J7.4, J10.3, J11.4, R20.1, U5.11
RX/SCL2: J13.4, J14.4, J16.3, J17.4, R31.1, U9.11
RX/SCL3: J19.4, J20.4, J22.3, J23.4, R42.1, U13.11
SCK: J5.3, U1.3, U2.6
SCK1: J12.3, U5.3, U6.6
SCK2: J18.3, U9.3, U10.6
SCK3: J24.3, U13.3, U14.6
SCL_S: R9.1, U1.20, U3.9, U4.9
SCL_S1: R18.1, U5.20, U7.9, U8.9
SCL_S2: R29.1, U9.20, U11.9, U12.9
SCL_S3: R40.1, U13.20, U15.9, U16.9
SDA_S: R10.1, U1.1, U3.10, U4.10
SDA_S1: R19.1, U5.1, U7.10, U8.10
SDA_S2: R30.1, U9.1, U11.10, U12.10
SDA_S3: R41.1, U13.1, U15.10, U16.10
TX/SDA: J1.3, J2.2, J4.3, J8.3, R12.1, U1.12
TX/SDA1: J6.3, J7.3, J10.2, J11.3, R21.1, U5.12
TX/SDA2: J13.3, J14.3, J16.2, J17.3, R32.1, U9.12
TX/SDA3: J19.3, J20.3, J22.2, J23.3, R43.1, U13.12

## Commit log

2018-10-15 Updating with Buzzard labels. Change logo to SparkFun. Change v to v10.
    [Qwiic_Spectral_Sensor-AS7265x.brd, Qwiic_Spectral_Sensor-AS7265x.sch]
2018-10-15 Removing old files
    [Q_Spec_Triad.GBL, Q_Spec_Triad.GBO, Q_Spec_Triad.GBS, Q_Spec_Triad.GKO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]
2018-10-16 Adding prod_ids to new parts
    [Qwiic_Spectral_Sensor-AS7265x.brd, Qwiic_Spectral_Sensor-AS7265x.sch]
2018-10-16 Moving board to origin
    [Qwiic_Spectral_Sensor-AS7265x.brd]
2018-10-16 Silk changes before panelization
    [Qwiic_Spectral_Sensor-AS7265x-BottomJig.brd, Qwiic_Spectral_Sensor-AS7265x-BottomJig.sch, Qwiic_Spectral_Sensor-AS7265x-MiddleJig.brd, Qwiic_Spectral_Sensor-AS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]
2018-10-16 Adding LED disconnect jumpers
    [Qwiic_Spectral_Sensor-AS7265x.brd, Qwiic_Spectral_Sensor-AS7265x.sch]
2018-10-16 Commit before panels
    [Qwiic_Spectral_Sensor-AS7265x.brd, Qwiic_Spectral_Sensor-AS7265x.sch]
2018-10-19 Adding panel
    [Qwiic_Spectral_Sensor-AS7265x-Panel.GBL, Qwiic_Spectral_Sensor-AS7265x-Panel.GBO, Qwiic_Spectral_Sensor-AS7265x-Panel.GBP, Qwiic_Spectral_Sensor-AS7265x-Panel.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]
2018-10-19 Adding Jig - It's called real jig to differentiate it from the Jig directory that is auto-generated a lot during jig testing.
    [Qwiic_Spectral_Sensor-AS7265x-BottomJig.brd, Qwiic_Spectral_Sensor-AS7265x-BottomJig.sch, Qwiic_Spectral_Sensor-AS7265x-MiddleJig.brd, Qwiic_Spectral_Sensor-AS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]
2018-10-19 Removing unneeded pass-through holes
    [Qwiic_Spectral_Sensor-AS7265x-BottomJig.brd, Qwiic_Spectral_Sensor-AS7265x-MiddleJig.brd]
2018-10-25 Intermediate committ. Probably ignore the jig files.
    [AS7265_CommandSet.xlsx, Qwiic_Spectral_Sensor-AS7265x-BottomJig.brd, Qwiic_Spectral_Sensor-AS7265x-BottomJig.sch, Qwiic_Spectral_Sensor-AS7265x-MiddleJig.GBL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]
2018-10-31 Adding test jig firmware
    [Qwiic_Spectral_Sensor-AS7265x-Offset-BottomJig.brd, Qwiic_Spectral_Sensor-AS7265x.brd]
2018-11-01 Update to schematic table. Update to readme.
    [Qwiic_Spectral_Sensor-AS7265x.brd, Qwiic_Spectral_Sensor-AS7265x.sch]
2018-11-08 Remvoing gerbers. Removing jig files. Rename datasheet. Clean up repo before post.
    [Qwiic_Spectral_Sensor-AS7265x-BottomJig.brd, Qwiic_Spectral_Sensor-AS7265x-BottomJig.sch, Qwiic_Spectral_Sensor-AS7265x-MiddleJig.GBL, Qwiic_Spectral_Sensor-AS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]

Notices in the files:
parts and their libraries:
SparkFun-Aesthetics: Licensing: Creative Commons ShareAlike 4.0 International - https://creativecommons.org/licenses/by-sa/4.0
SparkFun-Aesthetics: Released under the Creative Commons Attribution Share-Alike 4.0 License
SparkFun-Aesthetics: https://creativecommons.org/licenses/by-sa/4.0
